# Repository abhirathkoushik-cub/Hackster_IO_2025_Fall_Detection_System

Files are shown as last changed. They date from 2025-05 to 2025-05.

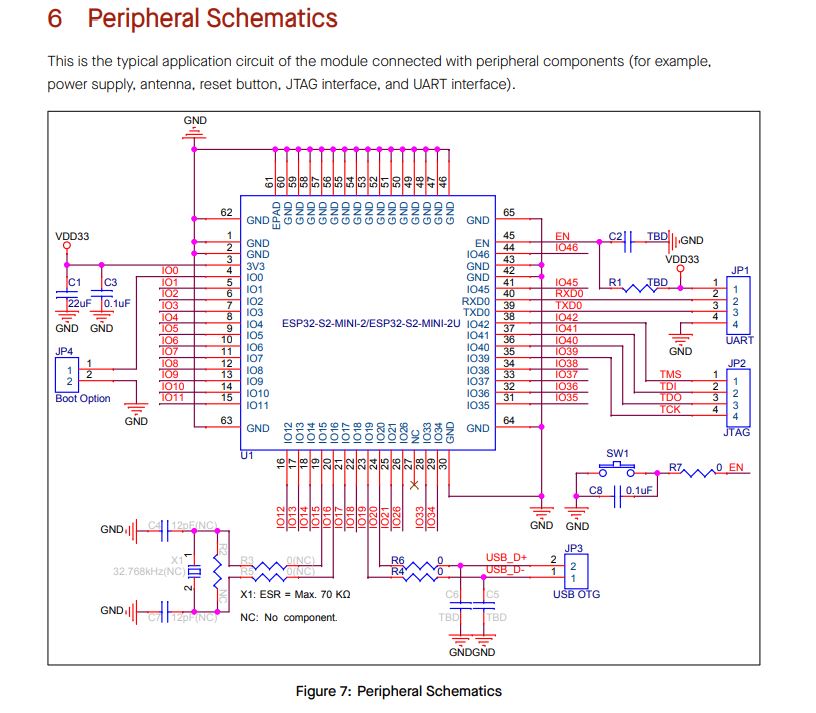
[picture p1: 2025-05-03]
Design Documentation/DATA_SHEETS/Capture1.JPG

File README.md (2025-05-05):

This Repository contains the Code, PCB and Schematic Files for the Sentinel-Fall: Smart Radar Based Fall Detection System project done for Hackster IO Competition 2025.

Project Link: https://www.hackster.io/sentinel-fall/sentinel-fall-smart-radar-based-fall-detection-system-265fd4#toc---step-2---firmware-programming---esp32--amp--nrf54l15-11 

Project Contributers: Abhirath Koushik, Nikhil Bhat and Vrushabh Gada

My Individual Contribution is for the NRF BLE Alert Configuring and Programming, 
https://github.com/abhirathkoushik-cub/Hackster_IO_2025_Fall_Detection_System/tree/main/Program%20Files/Demo%20Code%20Files/NRF%20BLE%20Alerts%20(Dev%20Kit)

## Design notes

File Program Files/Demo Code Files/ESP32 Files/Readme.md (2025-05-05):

# Author

Vrushabh Gada

# Software Tools:
    Arduino ide (Used to write and program the esp32)
# Hardware:
    ESP32

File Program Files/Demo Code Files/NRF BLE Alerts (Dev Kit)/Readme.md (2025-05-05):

## Author 
Abhirath Koushik (abhirathkoushik-cub)

# Software Tools:
1. nRF Connect VS Code Externsion (For Programming the nRF54L15 DK/SoC)
2. nRF Connect for Desktop (For viewing and interacting with the Serial Terminal)
3. nRF Connevt for Mobile (For viewing the BLE Alerts on the phone. Can also be used to send back a message and enable bi-directional communication)

# Hardware:
1. nRF54L15 DK
2. Arduino Uno (Used for testing my program by providing alternative high-low pulses on the GPIO Pin of the DK)

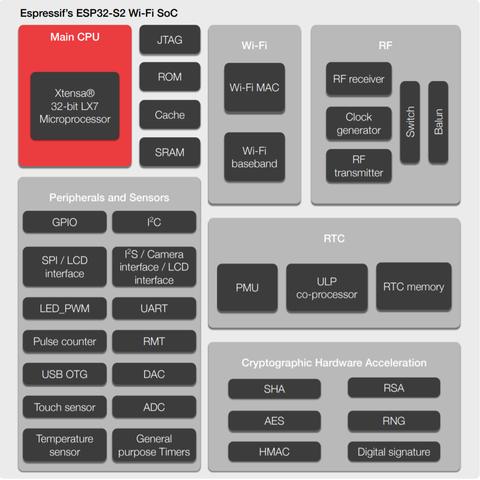
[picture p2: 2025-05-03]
Design Documentation/DATA_SHEETS/NRF_SOC/NRF_PROJ336/NRF_PROJ/param.jpg

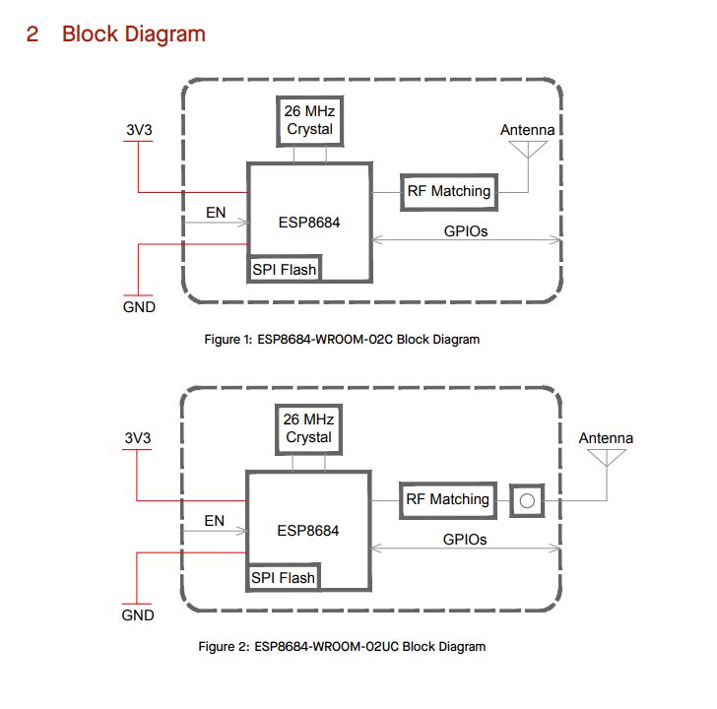
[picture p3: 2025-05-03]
Design Documentation/DATA_SHEETS/NRF_SOC/NRF_PROJ336/NRF_PROJ/Capture.JPG

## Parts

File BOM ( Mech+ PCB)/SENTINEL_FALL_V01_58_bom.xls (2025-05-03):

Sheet: SENTINEL_FALL_pcb_bom
Item | Quantity | Reference | Value | MFG Part Number | MFG Name | BOM NOTE | PCB Footprint
1 | 2 | C1,C37 | 10uF | CNC5L1X7R1H106K160AE | TDK | NA | C1206 | note: refer next sheet for mechanical bom
2 | 2 | C2,C17 | 1uF | C1206R105K3RACT250 | KEMET | NA | C1206
3 | 4 | C3,C6,C10,C73 | 4.7uF | CC1206KKX7R9BB475 | YAGEO | NA | C1206
4 | 14 | C4,C11,C12,C15,C18,C20,C21,C23,C24,C38,C39,C71,C72,C75 | 10uF | GCM31CD71H106KE36K | Murata Electronics | NA | C1206
5 | 1 | C5 | 47nF | C1206C473F5GECAUTO | KEMET | NA | C1206
6 | 3 | C7,C8,C9 | 22uF | C2012X5R1V226M125AC | TDK | NA | C0805
7 | 2 | C13,C14 | 47uF | GRM31CR61C476ME44K | Murata Electronics | NA | C1206
8 | 8 | C16,C25,C26,C27,C28,C30,C74,C76 | 100nF | C1206C104K5RACTU | KEMET | NA | C1206
9 | 2 | C29,C31 | 2.2uF | CL31B225KOHNNNE | Samsung Electro-Mechanics | NA | C1206
10 | 1 | C32 | 10nF | MSASU105SB7103KFNA01 | Taiyo Yuden | NA | C1206
11 | 3 | C33,C35,C36 | 18pF | VJ1206A180JXXPW1BC | Vishay Vitramon | NA | C1206
12 | 1 | D2 | DIODE | B260A-13-F | Diodes Inc | NA | DIOM5226X230N
13 | 1 | FB1 | 120R, 0.2A | BLM21RK121SN1D | Murata Electronics | NA | F0805
14 | 6 | FD1,FD2,FD3,FD4,FD5,FD6 | TEST POINT_SMD | NOT APPLICABLE | NOT APPLICABLE | NA | 40-t_global_fid
15 | 2 | J1,J8 | USB4105-GF-A | USB4105-GF-A | GCT | NA | GCT_USB4105-GF-A
16 | 2 | J5,J6 | 2X5 HDR JLINK | 3220-10-0300-00 | CNC Tech | NA | CNC_3220-10-0300-00
17 | 1 | J7 | HEADER 2/SM_5 | S2B-PH-SM4-TB | JST Sales America Inc. | NA | JST_S2B-PH-SM4-TB
18 | 1 | J11 | PH1-06-UA | PH1-06-UA | Adam Tech | NA | HDRV6W64P0X254_1X6_1524X250X952P
19 | 1 | L1 | 1uH | IHLP2525CZER1R0M01 | Vishay Dale | NA | IND_IHLP2525CZER1R0M01
20 | 1 | L2 | 4.7uH | MLZ1608M4R7WT000 | TDK Corporation | NA | L0603
21 | 7 | R2,R3,R14,R15,R32,R33,R34 | 10K | RC1206FR-0710KL | TE Connectivity | NA | R1206
22 | 12 | R4,R5,R12,R16,R19,R24,R27,R28,R29,R30,R35,R46 | 4K7 | RC1206FR-074K7L | YAEGO | NA | R1206
23 | 4 | R6,R7,R8,R9 | 4K7 | RC1206FR-074K7L | YAEGO | NA | R1206
24 | 2 | R10,R13 | 0R | RC1206JR-070RL | YAGEO | NA | R1206
25 | 2 | R11,R31 | 1M | TNPW12061M00BEEA | Vishay Dale | NA | R1206
26 | 1 | R17 | 1.05K, 0p1% | TNPW12061K05BEEN | Vishay / Dale | NA | R1206
27 | 1 | R18 | 6.8K,0p1% | ERA-8AEB682V | Panasonic Electronic Components | NA | R1206
28 | 6 | R23,R37,R39,R40,R41,R45 | 1K | RCWP12061K00FKS2 | Vishay / Dale | NA | R1206
29 | 2 | R26,R47 | 100R | RC1206FR-7W100RL | YAGEO | NA | R1206
30 | 1 | R36 | 500m | RCWE1206R500FKEA | Vishay Dale | NA | R1206
31 | 3 | R42,R43,R44 | 5k6 | ERJ-S08F5601V | Panasonic | NA | R1206
32 | 1 | SW1 | 500SSP3S1M6QEA | 500SSP3S1M6QEA | E-Switch | NA | 500SSP3S1M6QEA
33 | 3 | SW6,SW7,SW8 | SW_TC_SPST_1 | KMR221NGLFS | C&K | NA | KMR221_CNK
34 | 1 | SW9 | BD04AV | BD04AV | C&K | NA | BD04AV
35 | 10 | TP2,TP3,TP4,TP12,TP13,TP14,TP15,TP16,TP20,TP21 | TEST POINT_2 | NA | NA | NA | TP40
36 | 4 | TP6,TP17,TP18,TP19 | T POINT R | NA | NA | NA | mh7p5_3p2t
37 | 1 | U1 | TVS DIODE | TVS2200DRVR | TI | NA | SON65P200X200X80-7N
38 | 1 | U2 | BQ25886RGE | BQ25886RGER | Texas Instruments | NA | QFN50P400X400X100-25N
39 | 2 | U3,U4 | MYLSM00502ERPL | MYLSM00502ERPL | Murata | NA | MURATA_MYLSM00502ERPL
40 | 1 | U5 | MCP1727-3302ESN | MCP1727-3302E/SN | Microchip Technology | NA | SOIC127P600X175-8N
41 | 1 | U6 | ESP32-S3-MINI | ESP32-S3-MINI-1-N8 | Espressif Systems | NA | ESP32-S3-MINI-1U_EXP
42 | 1 | U7 | SIM8000L | SIM8000L MODULE | ElectroPeak 3.4/5 | NA | SIM8000L
43 | 4 | U8,U9,U10,U11 | IN-PI55QATPRPGPBPW-40 | IN-PI55QATPRPGPBPW-30 | Inolux | NA | INPI55QATPRPGPBPW30
44 | 1 | U12 | BC818-40LT1G | BC818-40LT1G | onsemi | NA | SOT95P237X111-3N
45 | 1 | U13 | AT-1224-TWT-5V-2-R | AT-1224-TWT-5V-2-R | PUI Audio, Inc. | NA | XDCR_AT-1224-TWT-5V-2-R
46 | 1 | U14 | NRF54L15-QFAA-R | NRF54L15-QFAA-R | Nordic Semiconductors | NA | QFN40P600X600X90-49N
47 | 1 | U15 | SEN0623 | SEN0623 | DF ROBOT | NA | SEN0623
48 | 1 | U16 | EKMB1101111 | EKMB1101111 | Panasonic Electric Works | NA | EKMB1101111
49 | 1 | U17 | SSM3J332R | SSM3J332R,LF | Toshiba Electronic Devices Storage Corp. | NA | SOT95P240X88-3N
50 | 1 | X1 | 32 MHz | MP06003 | Golledge Electronics Ltd | NA | XTAL_ABM11W-330000MHZ-8-D1X-T3
NOTE: | note: refer next sheet for mechanical bom

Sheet: MECH BOM
 | FASTNERS, SCREWS, NUTS
SL NO | DESCRIPTION | QTY
1 | 6-6 Male-Female Threaded Hex Standoff (M3X12) | 4
2 | Aluminum Hex Nut(M3) | 4
3 | Stainless Steel Hex Drive Flat Head Screw(M3X6) | 10
4 | 95610A104_Nylon Plastic Washer (M3) | 6
5 | Steel Socket Head Screw (M2.5X6) | 2
6 | Aluminum Hex Nut(M2.5) | 2
 | 3D PRINT FILES
SL NO | DESCRIPTION | QTY
1 | BOTTOM CONTAINER | 1
2 | TOP LID | 1
3 | BRACKET-1 | 1
4 | BRACKET-2 | 1
 | OTHER ITEMS
SL NO | DESCRIPTION | QTY | Link
1 | 7.4V 2600mAh Rechargeable Li-ion Battery with JST 2Pin, 2.0 | 1 | https://www.amazon.com/dp/B0DSZNX3YP?ref=ppx_yo2ov_dt_b_fed_asin_title
2 | Car Phone Holder Mobile Phone Holder Stand | 1 | https://www.aliexpress.us/item/3256802910592284.html
3 | Segger J link Cable | 1 | https://www.digikey.com/en/products/detail/adafruit-industries-llc/1675/6827142

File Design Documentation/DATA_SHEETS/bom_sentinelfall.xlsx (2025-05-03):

 | Component | Description | Quantity | Source
1 | nRF54L15 | Nordic Semiconductor BLE SoC | 1 | Nordic Semiconductor | finalized | https://www.mouser.com/ProductDetail/Nordic-Semiconductor/NRF54L15-CAAA-R?qs=QpmGXVUTftEz0ltGbbtKyA%3D%3D
2 | 101990981 | 24GHz mmWave Radar Module (Doppler Radar, Sleep Detection) | 1 | Seeed Studio | finalized | 101990981
3 | ESP32-S2FH4 | RF TXRX MOD WIFI PCB TRACE SMD | 1 | espressif | finalized | https://www.digikey.com/en/products/detail/espressif-systems/ESP32-S2FH4/14553010
4 | SIM800L | Smallest SIM800L GPRS GSM Breakout Module Quad-Band 850/900/1800/1900MHz SIM Card Slot Onboard with Antenna 3.7~4.2V | 1 | amazon |  | https://electropeak.com/sim800l-gprs-gsm-sms-microsim-module?gQT=2
5 | AM312 | HiLetgo 3pcs AM312 Mini Pyroelectric PIR Human Sensor Module PIR Infrared IR Sen | 1 |  |  | https://www.amazon.com/HiLetgo-Pyroelectric-Sensor-Infrared-Detector/dp/B07RT7MK7C
6 | BQ25306 | A 1-2 Cell Buck Battery Charger | 1
 | BQ25723 | Buck-Boost Battery Charger | 1 | Various Suppliers
 | ESP32-WROOM (Replacing EBYTE E34-2G4H in the design) | WiFi + BLE Module | 1 | Espressif
 | SIM800L | GSM Module with MIC & Headphone Jack | 1 | M5Stack
 | AM312 | Mini Pyroelectric PIR Sensor | 1 | Various Suppliers
 | Turnigy 5000mAh 4S 25C LiPo Pack w/XT-90 | High-capacity battery | 1 | Turnigy / HobbyKing

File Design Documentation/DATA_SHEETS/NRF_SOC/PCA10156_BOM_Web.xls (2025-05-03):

Bill of material
Board: | PCA10156
Version: | 0.8.1
Designator | Value | Description | Fitted | Footprint Doc | Manufacturer | Manufacturer Part Number
C1, C2 | 2.2µF | Capacitor, Ceramic, 2.2µF 2.5V X6T 0201,±20% | Fitted | 0201 | Murata | GRM033R61A225KE47
C3, C10 | 10µF | Capacitor, X6S, ±20%, 6.3V | Fitted | 0402 | N.A. | N.A.
C4, C7, C8, C11, C13, C14, C15, C16, C18, C20, C21, C22, C29, C34, C35, C36, C37, C44, C46, C48, C49, C52, C53, C55 | 100nF | Capacitor, X5R, ±10% | Fitted | 0201 | N.A. | N.A.
C5 | 18pF | Capacitor, C0G, ±5%, 25V | Fitted | 0201 | Walsin Technology Corporation | 0201N180J250CT
C6 | 0.9pF | Capacitor, C0G, ±0.1pF, 25V | Fitted | 0201 | Murata | GJM0335C1ER90BB01D
C9 | 0.6pF | Capacitor, C0G, ±0.1pF, 25V | Fitted | 0201 | Murata | GJM0335C1ER60BB01
C12, C30 | 10nF | Capacitor, X7R, ±10% | Fitted | 0201 | N.A. | N.A.
C17, C19 | 300pF | Capacitor, C0G, ±5%, 50V | Fitted | 0402 | N.A. | N.A.
C23 | 2.2µF | Capacitor, X5R, ±10% | Fitted | 0402 | N.A. | N.A.
C24, C25, C26, C27, C28 | 10µF | Capacitor, X7T, ±20%, 10V | Fitted | 0603 | Murata | GRM188D71A106MA73
C31, C32, C38, C39, C45 | 1.0µF | Capacitor, X5R, ±10%, 6.3V | Fitted | 0402 | N.A. | N.A.
C33 | 2.2nF | Capacitor, X7R, ±10%, 10V | Fitted | 0201 | N.A. | N.A.
C40 | 1.4pF | Capacitor, C0G, ±0.05pF, 25V | Fitted | 0201 | Murata | GJM0335C1E1R4WB01D
C41 | 100nF | Capacitor, X7R, ±10% | Not Fitted | 0402 | N.A. | N.A.
C42, C43, C54 | 4.7µF | Capacitor, X7S, ±10%, 10V | Fitted | 0603 | N.A. | N.A.
C47 | 1.0µF | Capacitor, Ceramic, X5R, ±10%, 16V | Fitted | 0402 | Murata | GRT155R61C105KE01D
C50 | 10nF | Capacitor, X7R, ±10% | Not Fitted | 0201 | N.A. | N.A.
C51 | TBD | Chip Cap 0201 | Not Fitted | 0201 | N.A. | N.A.
C56 | 100nF | Capacitor, X5R, ±10% | Not Fitted | 0201 | N.A. | N.A.
D1 | PRTR5V0U2X | Ultra low capacitance double rail-to-rail ESD protection diode | Fitted | SOT-143B | NXP Semiconductors | PRTR5V0U2X
FB1 | 120R/0.2A | Ferrite Bead, 120 Ohm @ 100MHz, 200mA, 500 mOhm Max | Fitted | 0201 | Murata | BLM03AG121SN1D
FB2 | 120R/0.55A | Ferrite Bead, 120 Ohm @ 100MHz, 500mA, 250 mOhm Max | Fitted | 0402 | Murata | BLM15AG121SN1D
Fid1, Fid2, Fid3 | N.A. | Fiducial Mark | Fitted | Fiducial | N.A. | N.A.
J1 | MM8130-2600 | Coaxial Connector with Switch | Fitted | COAXIAL-SWF | Murata | MM8130-2600
J3 | USB-C 2.0 | USB-C Receptacle, 16 Pin, USB 2.0 | Fitted | SD-80259-001 | Bellweather Electronic Corp. | SD-80259-1021
J7 | FPC 0.5mm RA SMD | 0.5mm FPC, 5P,Right Angle SMT,Double Contact,H=1.2mm,White, Tin plated | Fitted | FPC_05P-0.5mm-RA-SMD | WCON | 5141-05RZDNWR03
JP1 | Shunt 2.54mm | Shunt Jumper 2.54mm Black, open top | Fitted | SHUNT JUMPER 2.54mm | Samtec | SNT-100-BK-T
L1 | 4.7µH | Inductor, 120mA, ±20%, 0.65R | Fitted | 0603 | TDK Corporation | MLZ1608M4R7WT000
L2 | 1.6nH | Inductor, 1000mA, ±0.05ｎH, 50mOhm | Fitted | 0201 | Murata | LQP03HQ1N6W02
L3 | 3.5nH | Inductor, 500mA, ±0.1ｎH, 170mOhm | Fitted | 0201 | Murata | LQP03HQ3N5B02
L4 | 1.2nH | Inductor, 1100mA, ±0.05ｎH, 40mOhm | Fitted | 0201 | Murata | LQP03HQ1N2W02
L8, L9 | 2.2µH | Inductor, Irms=2.5A, Isat=2.9A, ±20%, DCR=73mΩ | Fitted | 0806 | Samsung Electro-Mechanics America | CIGT201610EH2R2MNE
LABEL1 | 12x12mm | PCA version label, stick-on, 12x12mm | Fitted | Label | Ellco Etikett | A33512‐01
LD1, LD2, LD3, LD4, LD5 | L0603G | LED, Green, 0603, 573nm, Vf=2.0V, 24mcd, - 40 to +85°C | Fitted | 0603 | Victory Electronics | VS 25C7M5
P0, P1, P2 | Pin Hdr 2x10 | Pin Header 2x10, 2.54mm (100mil) SMD | Fitted | HDR_2x10-SMD-2.54MM | WCON | 1125-1210S0M116CR09
P4 | Pin List 1x3 | Pin List 1x3, 2.54mm (100mil) | Not Fitted | LIST_1x3 | N.A. | N.A.
P6 | Pin List 1x3 | Pin List 1x3, 2.54mm (100mil), SMD | Fitted | LIST_1x3_SMD | WCON | 1125-1103S0M116CR04
P15, P19 | Pin Header 2x5, 1.27mm | Pin Header 2x5, 1.27mm (50mil), SMD, Keying Shroud | Fitted | HDR_2x5-SMD-1.27mm | WCON | 3132-10MS0BK00R5
P16 | Pin Header 2x10, 1.27mm | Pin Header 2x10, 1.27mm (50mil), SMD, Keying Shroud | Not Fitted | HDR_2x10-SMD-1.27mm | WCON | 3132-20MS0BK00R1
P30, P31, P32 | Pin Header 2x2 SMD | Pin Header 2x2, SMD, 2.54mm (100mil) | Fitted | HDR_2x2-SMD | WCON | 1125-1202S0M116CR03
Q1, Q2, Q3 | NX138AKS | MOSFET 2N-CH 60V 0.17A TSSOP6 (SOT363) | Fitted | TSSOP6 | Nexperia | NX138AKSX
Q6 | PBSS4330PA | 30V, 3A, 2.1W, G=270, NPN Transistor | Fitted | HUSON-3 (2x2) | Nexperia | PBSS4330PA,115
R1, R2, R19, R20 | 220R | Resistor, ±1%, 0.05W | Fitted | 0201 | N.A. | N.A.
R3 | 4k7 | Resistor, ±1%, 0.05W | Fitted | 0201 | N.A. | N.A.
R5 | 560R | Resistor, ±1%, 0.05W | Fitted | 0201 | N.A. | N.A.
R6, R8, R13, R14, R15, R16, R17, R23, R55, R56 | 100k | Resistor, ±1%, 0.05W | Fitted | 0201 | N.A. | N.A.
R7 | 47R | Resistor, ±1%, 0.05W | Fitted | 0201 | N.A. | N.A.
R10, R11, R12, R18, R27 | 1M0 | Resistor, ±1%, 0.05W | Fitted | 0201 | N.A. | N.A.
R21, R22 | 0R | Resistor, ±5%, 0.063W | Fitted | 0402 | N.A. | N.A.
R24 | TBD | Chip Res 0402 | Not Fitted | 0402 | N.A. | N.A.
R25 | 270k | Resistor, ±1%, 0.05W | Fitted | 0201 | N.A. | N.A.
R26 | 47k | Resistor, ±1%, 0.05W | Fitted | 0201 | N.A. | N.A.
R28 | 33k | Resistor, ±1%, 0.05W | Fitted | 0201 | N.A. | N.A.
R29, R30 | 18k | Resistor, ±1%, 0.05W | Not Fitted | 0201 | N.A. | N.A.
R31, R32, R35 | 0R | Resistor, ±5%, 0.05W | Fitted | 0201 | N.A. | N.A.
R33, R34 | 0R | Resistor, ±5%, 0.063W | Not Fitted | 0402 | N.A. | N.A.
R36 | 1k | Resistor, ±1%, 0.05W | Fitted | 0201 | N.A. | N.A.
R54 | 0R | Resistor, ±5%, 0.05W | Not Fitted | 0201 | N.A. | N.A.
SW1, SW2, SW3, SW5, SW6 | PB SW | Tactile Switch, SPNO, SMD, 160gf, 6.2x6.3x2.5mm | Fitted | Switch-PB-6.2x6.3mm-SMD | Dailywell | TS604VM1-025BR-R
SW4 | MK-22D14-G2 | Slide Switch DPDT | Fitted | MK-22D14-G2 | HUA-JIE CORP. | MK-22D14-G2
TP22 | TP | PC TEST POINT TIN SMD L | Fitted | Harwin S1751-46R | Harwin | S1751-46R
U1 | nRF54L15-QFAABB0 | Multi-protocol Bluetooth Low Energy, IEEE 802.15.4, ANT and 2.4GHz proprietary system-on-chip | Fitted | QFN-48 | Nordic Semiconductor | nRF54L15-QFAABB0
U2 | nRF5340-QKAA | Multi-protocol Bluetooth Low Energy, IEEE 802.15.4, ANT and 2.4GHz proprietary system-on-chip | Fitted | AQFN-98 | Nordic Semiconductor | nRF5340-QKAAD0
U3 | TLV271 | Dual rail to rail CMOS Amplifier | Fitted | SOT-25 | Diodes Incorporated | TLV271CW5-7
U4, U5, U6 | FSA2466UMX | Data / Audio Low-Voltage Dual DPDT Analog Switch | Fitted | UFQFN-16 | ON Semiconductor | FSA2466UMX
U7, U8 | TXB0302 | 2-bit bidirectional voltage-level translator with automatic direction sensing | Fitted | XFDFN-8 | Texas Instruments | TXB0302DQMR
U9 | MX25R6435F | Ultra low power, 64M-bit, serial multi I/O flash memory | Fitted | WSON-8 | Macronix | MX25R6435FZNIL0
U10 | nPM1300-QEAAC0 | Li-Ion/Li-Polymer USB-C battery charger with high efficiency buck regulators, LDOs or load switches, LED drivers, TWI and VBUSOUT | Fitted | QFN-32 | Nordic Semiconductor | nPM1300-QEAAC0
X1 | 32.768kHz | XTAL SMD 2012, 32.768kHz, 9pF, ±20ppm | Fitted | XTAL_2012 | TXC Corporation | 9HT11-32.768KDZC-T
X2, X3 | 32MHz | XTAL SMD 2016, 32MHz, Cl=8pF, Tol: ±10ppm, Stab: ±15ppm | Fitted | XTAL_2016 | Golledge | MP06003
 |  | Pin Header 2x5, 1.27mm

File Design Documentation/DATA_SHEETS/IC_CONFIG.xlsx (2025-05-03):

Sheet: Sheet1
 | Component | Description | Quantity | Source
1 | nRF54L15 | Nordic Semiconductor BLE SoC | 1 | Nordic Semiconductor | finalized | https://www.mouser.com/ProductDetail/Nordic-Semiconductor/NRF54L15-CAAA-R?qs=QpmGXVUTftEz0ltGbbtKyA%3D%3D
2 | 101990981 | 24GHz mmWave Radar Module (Doppler Radar, Sleep Detection) | 1 | Seeed Studio | finalized | 101990981
3 | ESP32-S2-SOLO-2-N4 | RF TXRX MOD WIFI PCB TRACE SMD | 1 | espressif | finalized | https://www.digikey.com/en/products/detail/espressif-systems/ESP32-S2FH4/14553010
4 | SIM800L | Smallest SIM800L GPRS GSM Breakout Module Quad-Band 850/900/1800/1900MHz SIM Card Slot Onboard with Antenna 3.7~4.2V | 1 | amazon | finalized | https://electropeak.com/sim800l-gprs-gsm-sms-microsim-module?gQT=2
5 | AM312 | HiLetgo 3pcs AM312 Mini Pyroelectric PIR Human Sensor Module PIR Infrared IR Sen | 1 | amazon | finalized | https://www.amazon.com/HiLetgo-Pyroelectric-Sensor-Infrared-Detector/dp/B07RT7MK7C
6 | BQ25886 | A 1-2 Cell Buck Battery Charger | 1 | amazon | finalized
 |  | PWR RAILS
 |  | 5 | 3.3 | 4 | PWR
1 | nRF54L15 |  | 80 |  | 264
2 | 101990981 | 100 |  |  | 500
3 | ESP32-S2-SOLO-2-N4 |  | 500 |  | 1650
4 | SIM800L |  |  | 2000 | 8000 | PEAK
5 | AM312 |  | 1 |  | 3.3
 |  |  |  |  | 10.4173 | PEAK
 |  | 100 | 581
 |  | 0.1A | 3.3A | 2A
 |  | PWR TREE
 |  | tell me 1 ldo THAT can convert from 2s batetry to 5v, 5v to 3v3 , 5v to 4v .
 |  |  | LTM4705 | FOR 3V3
 |  |  | TPS7B82-Q1 | FOR 5V0
 | BQ25723 | Buck-Boost Battery Charger | 1 | Various Suppliers
 | ESP32-WROOM (Replacing EBYTE E34-2G4H in the design) | WiFi + BLE Module | 1 | Espressif
 | SIM800L | GSM Module with MIC & Headphone Jack | 1 | M5Stack
 | AM312 | Mini Pyroelectric PIR Sensor | 1 | Various Suppliers
 | Turnigy 5000mAh 4S 25C LiPo Pack w/XT-90 | High-capacity battery | 1 | Turnigy / HobbyKing

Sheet: Sheet4
https://www.mouser.com/ProductDetail/Texas-Instruments/TPSM84338RCJR?qs=7%2F6SraaimPTVMRXxZgYtyw%3D%3D
MYLSM00502ERPL

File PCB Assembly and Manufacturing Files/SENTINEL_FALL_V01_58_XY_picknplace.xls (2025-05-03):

Design Name E:/nn/GERBER/BOARD/SENTINEL_FALL_V01.brd
Date Tue Apr 08 22:40:18 2025
Total Placed Components: &nbsp136
Placed Component Report
REFDES | COMP_DEVICE_TYPE | COMP_VALUE | COMP_TOL | SYM_NAME | SYM_X | SYM_Y | SYM_ROTATE | SYM_MIRROR
C1 | CAP_CER_10UF_50V_1206_X7R_10P_C | 10uF |  | C1206 | 1649 | 2868 | 270 | NO
C2 | CAP_1UF_25V_1206_10P0_C1206_1UF | 1uF |  | C1206 | 1413.472 | 2123 | 90 | YES
C3 | CAP_CER_4700NF_50V_X7R_1206_C12 | 4.7uF |  | C1206 | 2105 | 2755 | 0 | NO
C4 | CAP_10UF_50V X7T_1206_C1206_10U | 10uF |  | C1206 | 1508 | 2123 | 270 | YES
C5 | 8_CAP_47NF_1206_C1206_47NF | 47nF |  | C1206 | 1930 | 2280 | 270 | YES
C6 | CAP_CER_4700NF_50V_X7R_1206_C12 | 4.7uF |  | C1206 | 2155 | 2580 | 90 | NO
C7 | 4_CAP_ 22UF 20% X5R_0805 35VDC_ | 22uF |  | C0805 | 1711 | 2421 | 180 | YES
C8 | 4_CAP_ 22UF 20% X5R_0805 35VDC_ | 22uF |  | C0805 | 1711 | 2338 | 180 | YES
C9 | 4_CAP_ 22UF 20% X5R_0805 35VDC_ | 22uF |  | C0805 | 1711 | 2505.213 | 180 | YES
C10 | CAP_CER_4700NF_50V_X7R_1206_C12 | 4.7uF |  | C1206 | 1578 | 2654 | 270 | YES
C11 | CAP_10UF_50V X7T_1206_C1206_10U | 10uF |  | C1206 | 1430 | 2485 | 0 | NO
C12 | CAP_10UF_50V X7T_1206_C1206_10U | 10uF |  | C1206 | 916.118 | 2459 | 180 | NO
C13 | CAP_CER_47UF_16V_X5R_1206_C1206 | 47uF |  | C1206 | 1258 | 2085.016 | 270 | NO
C14 | CAP_CER_47UF_16V_X5R_1206_C1206 | 47uF |  | C1206 | 566 | 2137 | 180 | NO
C15 | CAP_10UF_50V X7T_1206_C1206_10U | 10uF |  | C1206 | 2055 | 2365 | 90 | NO
C16 | CAP_100NF_50V_1206_X7R_C1206_10 | 100nF |  | C1206 | 2042 | 2075 | 270 | YES
C17 | CAP_1UF_25V_1206_10P0_C1206_1UF | 1uF |  | C1206 | 1825 | 2095 | 90 | NO
C18 | CAP_10UF_50V X7T_1206_C1206_10U | 10uF |  | C1206 | 1800 | 1070 | 270 | NO
C20 | CAP_10UF_50V X7T_1206_C1206_10U | 10uF |  | C1206 | 1896 | 1070 | 270 | NO
C21 | CAP_10UF_50V X7T_1206_C1206_10U | 10uF |  | C1206 | 174 | 2728 | 0 | NO
C23 | CAP_10UF_50V X7T_1206_C1206_10U | 10uF |  | C1206 | 350 | 1052.738 | 90 | NO
C24 | CAP_10UF_50V X7T_1206_C1206_10U | 10uF |  | C1206 | 540 | 575 | 180 | NO
C25 | CAP_100NF_50V_1206_X7R_C1206_10 | 100nF |  | C1206 | 930 | 1015 | 0 | NO
C26 | CAP_100NF_50V_1206_X7R_C1206_10 | 100nF |  | C1206 | 255.013 | 1052.738 | 90 | NO
C27 | CAP_100NF_50V_1206_X7R_C1206_10 | 100nF |  | C1206 | 930 | 920 | 0 | NO
C28 | CAP_100NF_50V_1206_X7R_C1206_10 | 100nF |  | C1206 | 316 | 783 | 180 | NO
C29 | CAP_CER_2.2UF_16V_X7R_1206_C120 | 2.2uF |  | C1206 | 406 | 1372 | 0 | YES
C30 | CAP_100NF_50V_1206_X7R_C1206_10 | 100nF |  | C1206 | 628 | 423 | 90 | NO
C31 | CAP_CER_2.2UF_16V_X7R_1206_C120 | 2.2uF |  | C1206 | 900 | 770 | 0 | NO
C32 | 7_CAP_10NF_10P_50V_C1206_10NF | 10nF |  | C1206 | 783 | 1471 | 180 | YES
C33 | CAP_18PF_125V_1206_C1206_18PF | 18pF |  | C1206 | 783 | 1372 | 180 | YES
C35 | CAP_18PF_125V_1206_C1206_18PF | 18pF |  | C1206 | 1010.137 | 606.252 | 180 | NO
C36 | CAP_18PF_125V_1206_C1206_18PF | 18pF |  | C1206 | 1230.609 | 606.252 | 0 | NO
C37 | CAP_CER_10UF_50V_1206_X7R_10P_C | 10uF |  | C1206 | 1076.567 | 2868 | 270 | NO
C38 | CAP_10UF_50V X7T_1206_C1206_10U | 10uF |  | C1206 | 1801 | 1790 | 90 | NO
C39 | CAP_10UF_50V X7T_1206_C1206_10U | 10uF |  | C1206 | 1925 | 2095 | 270 | NO
C71 | CAP_10UF_50V X7T_1206_C1206_10U | 10uF |  | C1206 | 1597 | 609 | 0 | NO
C72 | CAP_10UF_50V X7T_1206_C1206_10U | 10uF |  | C1206 | 1155 | 1785 | 270 | NO
C73 | CAP_CER_4700NF_50V_X7R_1206_C12 | 4.7uF |  | C1206 | 2182 | 580 | 90 | NO
C74 | CAP_100NF_50V_1206_X7R_C1206_10 | 100nF |  | C1206 | 2150 | 2365 | 90 | NO
C75 | CAP_10UF_50V X7T_1206_C1206_10U | 10uF |  | C1206 | 285 | 605 | 270 | NO
C76 | CAP_100NF_50V_1206_X7R_C1206_10 | 100nF |  | C1206 | 1850 | 1615 | 0 | NO
D2 | B260A-13-F_DIOM5226X230N_DIODE | DIODE |  | DIOM5226X230N | 460 | 1621 | 270 | YES
FB1 | FB_120R_200MA_0805_F0805_120R, | 120R, 0.2A |  | F0805 | 597 | 1372 | 180 | YES
FD1 | TEST POINT_SMD_0_40-T_GLOBAL_FI | TEST POINT_SMD |  | 40-T_GLOBAL_FID | 385 | 100 | 0 | NO
FD2 | TEST POINT_SMD_0_40-T_GLOBAL_FI | TEST POINT_SMD |  | 40-T_GLOBAL_FID | 385 | 100 | 0 | YES
FD3 | TEST POINT_SMD_0_40-T_GLOBAL_FI | TEST POINT_SMD |  | 40-T_GLOBAL_FID | 1985 | 100 | 0 | YES
FD4 | TEST POINT_SMD_0_40-T_GLOBAL_FI | TEST POINT_SMD |  | 40-T_GLOBAL_FID | 1985 | 100 | 0 | NO
FD5 | TEST POINT_SMD_0_40-T_GLOBAL_FI | TEST POINT_SMD |  | 40-T_GLOBAL_FID | 385 | 3215 | 0 | NO
FD6 | TEST POINT_SMD_0_40-T_GLOBAL_FI | TEST POINT_SMD |  | 40-T_GLOBAL_FID | 385 | 3215 | 0 | YES
J1 | CONN_USB_USB4105-GF-A_GCT_USB41 | USB4105-GF-A |  | GCT_USB4105-GF-A | 1726 | 3251 | 180 | NO
J5 | HEADER_10_2X5_SHROUDED_CNC_3220 | 2X5 HDR JLINK |  | CNC_3220-10-0300-00 | 2133 | 1160 | 90 | NO
J6 | HEADER_10_2X5_SHROUDED_CNC_3220 | 2X5 HDR JLINK |  | CNC_3220-10-0300-00 | 1585 | 245 | 0 | NO
J7 | HEADER 2/SM_5_JST_S2B-PH-SM4-TB | HEADER 2/SM_5 |  | JST_S2B-PH-SM4-TB | 314.189 | 2473 | 90 | NO
J8 | CONN_USB_USB4105-GF-A_GCT_USB41 | USB4105-GF-A |  | GCT_USB4105-GF-A | 1088.567 | 3251 | 180 | NO
J11 | HEADER_6_6X1_MALE_HDRV6W64P0X25 | PH1-06-UA |  | HDRV6W64P0X254_1X6_1524X250X952P | 519.96 | 220.75 | 0 | NO
L1 | IND_1UH_11A_1_UKPKG_IND_IHLP252 | 1uH |  | IND_IHLP2525CZER1R0M01 | 1711 | 2101 | 270 | YES
L2 | IND_4.7UH_350MA_500MOHM_SM_L060 | 4.7uH |  | L0603 | 472 | 1115 | 0 | NO
R2 | RES_10K_1W4_1P0_1206_R1206_10K | 10K |  | R1206 | 1657.102 | 2868 | 90 | YES
R3 | RES_10K_1W4_1P0_1206_R1206_10K | 10K |  | R1206 | 1775.213 | 2868 | 90 | YES
R4 | RES_4K7_1W4_1P0_1206_R1206_4K7 | 4K7 |  | R1206 | 1178 | 2316 | 180 | YES
R5 | RES_4K7_1W4_1P0_1206_R1206_4K7 | 4K7 |  | R1206 | 1387 | 2654 | 90 | YES
R6 | RES_4K7_1W4_1P0_1206_R1206_4K7 | 4K7 |  | R1206 | 1128 | 2123 | 270 | YES
R7 | RES_4K7_1W4_1P0_1206_R1206_4K7 | 4K7 |  | R1206 | 1223 | 2123 | 270 | YES
R8 | RES_4K7_1W4_1P0_1206_R1206_4K7 | 4K7 |  | R1206 | 1033 | 2123 | 90 | YES
R9 | RES_4K7_1W4_1P0_1206_R1206_4K7 | 4K7 |  | R1206 | 1318 | 2123 | 90 | YES
R10 | RES_0R0_1W4_1P0_1206_R1206_0R | 0R |  | R1206 | 1292 | 2654 | 270 | YES
R11 | RES_1M_1W2_0P1_1206_R1206_1M | 1M |  | R1206 | 1178 | 2507 | 0 | YES
R12 | RES_4K7_1W4_1P0_1206_R1206_4K7 | 4K7 |  | R1206 | 1482 | 2654 | 270 | YES
R13 | RES_0R0_1W4_1P0_1206_R1206_0R | 0R |  | R1206 | 1178 | 2412 | 0 | YES
R14 | RES_10K_1W4_1P0_1206_R1206_10K | 10K |  | R1206 | 1578 | 2654 | 90 | NO
R15 | RES_10K_1W4_1P0_1206_R1206_10K | 10K |  | R1206 | 1674 | 2654 | 270 | NO
R16 | RES_4K7_1W4_1P0_1206_R1206_4K7 | 4K7 |  | R1206 | 1248 | 2336.984 | 90 | NO
R17 | RES_1P05K_0W52_0P1_1206_R1206_1 | 1.05K, 0p1% |  | R1206 | 1729 | 2195.252 | 90 | NO
R18 | RES_6P8K_1W4_0P1_1206_R1206_6.8 | 6.8K,0p1% |  | R1206 | 1094 | 2192.252 | 90 | NO
R19 | RES_4K7_1W4_1P0_1206_R1206_4K7 | 4K7 |  | R1206 | 618 | 2333.984 | 90 | NO
R23 | RES_1K_1W4_1P0_1206_R1206_1K | 1K |  | R1206 | 1238 | 456 | 90 | YES
R24 | RES_4K7_1W4_1P0_1206_R1206_4K7 | 4K7 |  | R1206 | 1745 | 1940 | 0 | NO
R26 | RES_100R_1W8_1P0_1206_R1206_100 | 100R |  | R1206 | 797 | 1687 | 270 | YES
R27 | RES_4K7_1W4_1P0_1206_R1206_4K7 | 4K7 |  | R1206 | 723 | 423 | 270 | NO
R28 | RES_4K7_1W4_1P0_1206_R1206_4K7 | 4K7 |  | R1206 | 586.627 | 1181.748 | 90 | NO
R29 | RES_4K7_1W4_1P0_1206_R1206_4K7 | 4K7 |  | R1206 | 681.627 | 1181.748 | 90 | NO
R30 | RES_4K7_1W4_1P0_1206_R1206_4K7 | 4K7 |  | R1206 | 2182 | 774 | 270 | NO
R31 | RES_1M_1W2_0P1_1206_R1206_1M | 1M |  | R1206 | 1120.373 | 498.252 | 0 | NO
R32 | RES_10K_1W4_1P0_1206_R1206_10K | 10K |  | R1206 | 524 | 2334 | 270 | NO
R33 | RES_10K_1W4_1P0_1206_R1206_10K | 10K |  | R1206 | 1019.669 | 2868 | 90 | YES
R34 | RES_10K_1W4_1P0_1206_R1206_10K | 10K |  | R1206 | 1137.78 | 2868 | 90 | YES
R35 | RES_4K7_1W4_1P0_1206_R1206_4K7 | 4K7 |  | R1206 | 316 | 879.407 | 180 | NO
R36 | RES_500MOHM_1W2_1P0_1206_R1206_ | 500m |  | R1206 | 2050 | 2580 | 90 | NO
R37 | RES_1K_1W4_1P0_1206_R1206_1K | 1K |  | R1206 | 660.788 | 2971 | 180 | NO
R39 | RES_1K_1W4_1P0_1206_R1206_1K | 1K |  | R1206 | 655 | 2735 | 180 | NO
R40 | RES_1K_1W4_1P0_1206_R1206_1K | 1K |  | R1206 | 457.638 | 3055 | 0 | NO
R41 | RES_1K_1W4_1P0_1206_R1206_1K | 1K |  | R1206 | 406.235 | 2151.495 | 90 | NO
R42 | RES_GENRIC_5K6_1W4_1P0_1206_R12 | 5k6 |  | R1206 | 449.764 | 2735 | 0 | NO
R43 | RES_GENRIC_5K6_1W4_1P0_1206_R12 | 5k6 |  | R1206 | 347.402 | 2950 | 0 | NO
R44 | RES_GENRIC_5K6_1W4_1P0_1206_R12 | 5k6 |  | R1206 | 305.377 | 2096.08 | 0 | NO
R45 | RES_1K_1W4_1P0_1206_R1206_1K | 1K |  | R1206 | 1625 | 1776.882 | 90 | NO
R46 | RES_4K7_1W4_1P0_1206_R1206_4K7 | 4K7 |  | R1206 | 2210 | 1810 | 270 | NO
R47 | RES_100R_1W8_1P0_1206_R1206_100 | 100R |  | R1206 | 1135 | 566.236 | 90 | YES
SW1 | SWITH_PWR_RA_0_500SSP3S1M6QEA_5 | 500SSP3S1M6QEA |  | 500SSP3S1M6QEA | 1905 | 2510 | 90 | YES
SW6 | SW_TC_SPST_1_KMR221_CNK_SW_TC_S | SW_TC_SPST_1 |  | KMR221_CNK | 1989 | 1814.002 | 0 | NO
SW7 | SW_TC_SPST_1_KMR221_CNK_SW_TC_S | SW_TC_SPST_1 |  | KMR221_CNK | 718 | 3178.002 | 0 | NO
SW8 | SW_TC_SPST_1_KMR221_CNK_SW_TC_S | SW_TC_SPST_1 |  | KMR221_CNK | 455 | 398.998 | 180 | NO
SW9 | SW_RA_DIP_BD04AV_BD04AV | BD04AV |  | BD04AV | 2042.422 | 800.988 | 90 | YES
TP2 | TEST POINT_2_TP40_TEST POINT_2 | TEST POINT_2 |  | TP40 | 1825 | 2990 | 0 | NO
TP3 | TEST POINT_2_TP40_TEST POINT_2 | TEST POINT_2 |  | TP40 | 2050 | 2840 | 180 | NO
TP4 | TEST POINT_2_TP40_TEST POINT_2 | TEST POINT_2 |  | TP40 | 504.813 | 3183.242 | 0 | NO
TP6 | T POINT R_MH7P5_3P2T_T POINT R | T POINT R |  | MH7P5_3P2T | 160 | 3192.75 | 0 | NO
TP12 | TEST POINT_2_TP40_TEST POINT_2 | TEST POINT_2 |  | TP40 | 646 | 2551 | 0 | NO
TP13 | TEST POINT_2_TP40_TEST POINT_2 | TEST POINT_2 |  | TP40 | 1169.567 | 2927 | 0 | NO
TP14 | TEST POINT_2_TP40_TEST POINT_2 | TEST POINT_2 |  | TP40 | 1197.013 | 183.738 | 180 | YES
TP15 | TEST POINT_2_TP40_TEST POINT_2 | TEST POINT_2 |  | TP40 | 1931.813 | 187.222 | 0 | NO
TP16 | TEST POINT_2_TP40_TEST POINT_2 | TEST POINT_2 |  | TP40 | 1410.813 | 3081.882 | 0 | NO
TP17 | T POINT R_MH7P5_3P2T_T POINT R | T POINT R |  | MH7P5_3P2T | 160 | 160 | 0 | NO
TP18 | T POINT R_MH7P5_3P2T_T POINT R | T POINT R |  | MH7P5_3P2T | 2202.133 | 3192.75 | 0 | NO
TP19 | T POINT R_MH7P5_3P2T_T POINT R | T POINT R |  | MH7P5_3P2T | 2202.133 | 160 | 0 | NO
TP20 | TEST POINT_2_TP40_TEST POINT_2 | TEST POINT_2 |  | TP40 | 2250 | 2555 | 0 | NO
TP21 | TEST POINT_2_TP40_TEST POINT_2 | TEST POINT_2 |  | TP40 | 1885 | 1925 | 0 | NO
U1 | IC_TVS_DIODE_SON65P200X200X80-7 | TVS DIODE |  | SON65P200X200X80-7N | 1762 | 2867 | 90 | NO
U2 | BQ25886RGER_QFN50P400X400X100-2 | BQ25886RGE |  | QFN50P400X400X100-25N | 1472 | 2391 | 180 | YES
U3 | MYLSM00502ERPL_MURATA_MYLSM0050 | MYLSM00502ERPL |  | MURATA_MYLSM00502ERPL | 1481 | 2211 | 180 | NO
U4 | MYLSM00502ERPL_MURATA_MYLSM0050 | MYLSM00502ERPL |  | MURATA_MYLSM00502ERPL | 861 | 2208 | 180 | NO
U5 | MCP1727-3302ESN_SOIC127P600X175 | MCP1727-3302ESN |  | SOIC127P600X175-8N | 2100 | 2110 | 90 | NO
U6 | ESP32-S3-MINI_ESP32-S3-MINI-1U_ | ESP32-S3-MINI |  | ESP32-S3-MINI-1U_EXP | 1393 | 1172 | 180 | NO
U7 | SIP_IC_SIM800L_0_SIM8000L_SIM80 | SIM8000L |  | SIM8000L | 708.032 | 1983.74 | 270 | YES
U8 | IN-PI55QATPRPGPBPW-40_INPI55QAT | IN-PI55QATPRPGPBPW-40 |  | INPI55QATPRPGPBPW30 | 1446.284 | 448.126 | 0 | YES
U9 | IN-PI55QATPRPGPBPW-40_INPI55QAT | IN-PI55QATPRPGPBPW-40 |  | INPI55QATPRPGPBPW30 | 1731 | 447 | 90 | YES
U10 | IN-PI55QATPRPGPBPW-40_INPI55QAT | IN-PI55QATPRPGPBPW-40 |  | INPI55QATPRPGPBPW30 | 1731 | 741 | 180 | YES
U11 | IN-PI55QATPRPGPBPW-40_INPI55QAT | IN-PI55QATPRPGPBPW-40 |  | INPI55QATPRPGPBPW30 | 1446.284 | 741 | 270 | YES
U12 | NPN_TRANSISTOR_BC818-40LT1G_SOT | BC818-40LT1G |  | SOT95P237X111-3N | 631.221 | 1704.055 | 0 | YES
U13 | BUZZER_AT-1224-TWT-5V-2-R_XDCR_ | AT-1224-TWT-5V-2-R |  | XDCR_AT-1224-TWT-5V-2-R | 332 | 1621 | 180 | NO
U14 | NRF54L15-QFAA-R_QFN40P600X600X9 | NRF54L15-QFAA-R |  | QFN40P600X600X90-49N | 586.627 | 838.126 | 0 | NO
U15 | SIP_SEN0623_SEN0623_SEN0623 | SEN0623 |  | SEN0623 | 144 | 553 | 180 | YES
U16 | PIR_SIP_EKMB1101111_EKMB1101111 | EKMB1101111 |  | EKMB1101111 | 1288 | 1732 | 0 | YES
U17 | SSM3J332R,LF_SOT95P240X88-3N_SS | SSM3J332R |  | SOT95P240X88-3N | 517 | 2515 | 90 | NO
X1 | XTAL_32MHZ_XTAL_ABM11W-330000MH | 32 MHz |  | XTAL_ABM11W-330000MHZ-8-D1X-T3 | 1126.373 | 378.252 | 90 | NO

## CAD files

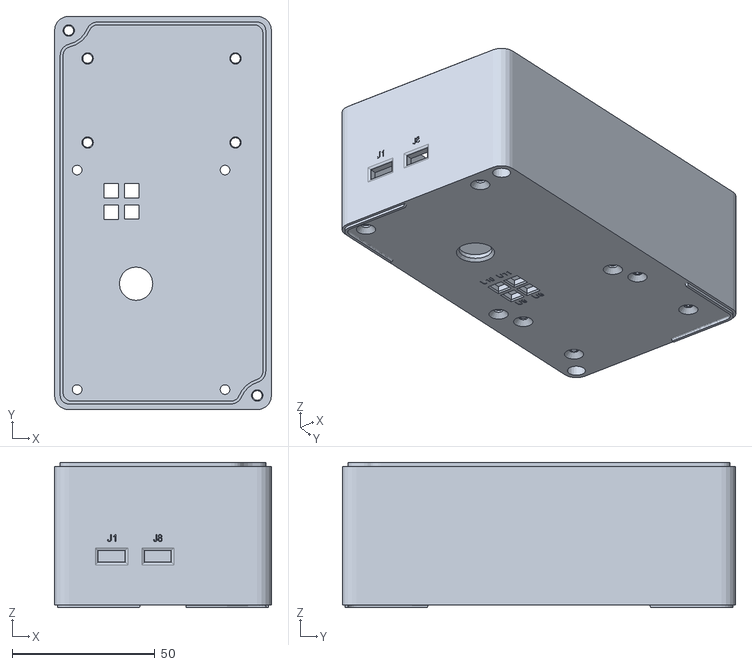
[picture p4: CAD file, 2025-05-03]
3D Files ( Top, Bottom Lid, Mounting Brackets)/MOUNTING CONTAINER BOTTOM PART_stp.stl
76.1 x 138.0 x 51.0

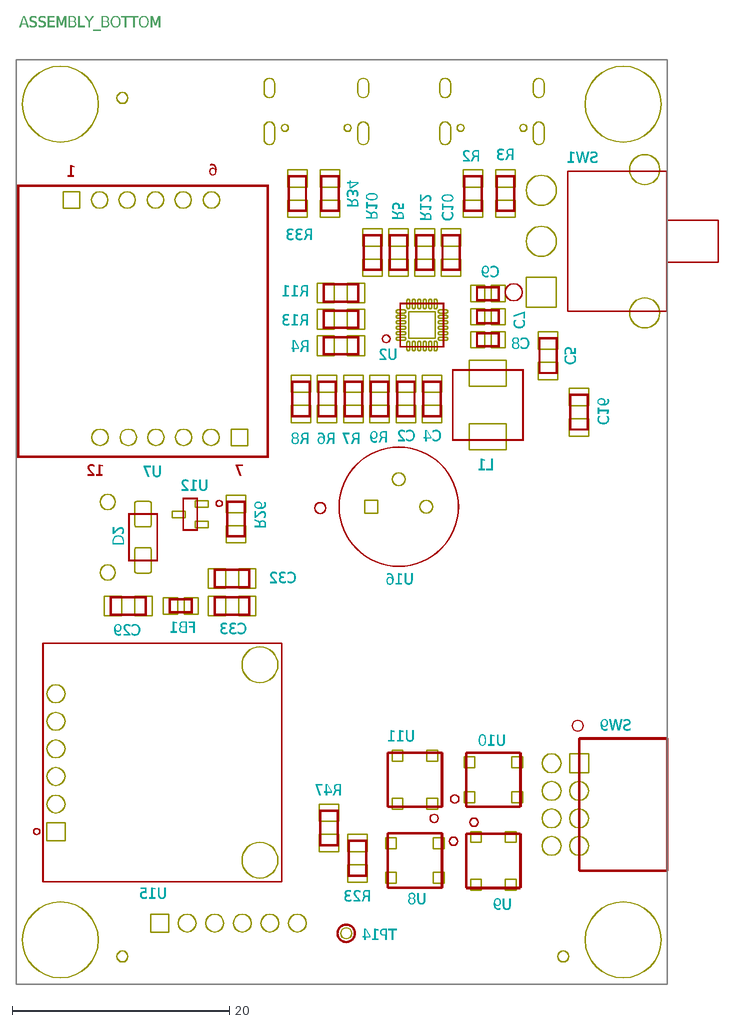
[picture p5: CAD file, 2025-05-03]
PCB Assembly and Manufacturing Files/MECHANICAL/DXF/BOTTOM.dxf
U12
D2
U11
U8
U10
U9
L1
C33
C29
C10
C16
C2
C4
C5
C32
R8
R10
R4
R3
R12
R13
R2
R23
R7
R6
R11
R9
R26
R33
R5
R34
R47
TP14
C9
C8
C7
U2
FB1
6
1
7
12
U7
U15
SW9
U16
SW1
ASSEMBLY_BOTTOM

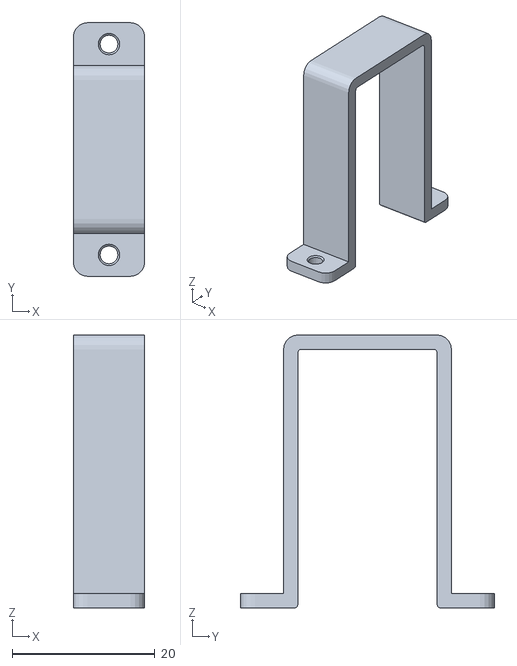
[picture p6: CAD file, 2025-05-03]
3D Files ( Top, Bottom Lid, Mounting Brackets)/BRACKET.stl
10.0 x 35.5 x 38.2

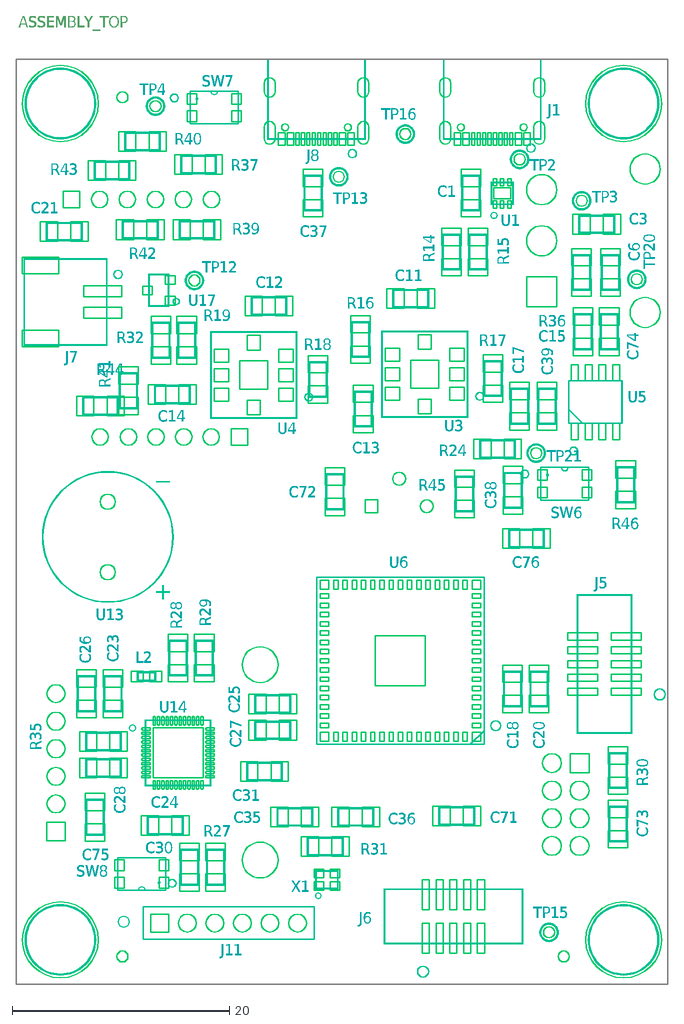
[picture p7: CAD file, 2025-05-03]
PCB Assembly and Manufacturing Files/MECHANICAL/DXF/TOP.dxf
X1
U17
J7
U5
U1
U6
C76
C35
C36
C31
C6
C3
C37
C12
C1
C17
C11
C15
C18
C20
C21
C23
C24
C38
C25
C14
C26
C27
C28
C30
C13
C72
C39
C71
C73
C75
C74
R42
R43
R44
R18
R19
R24
R14
R15
R16
R17
R31
R32
R29
R30
R27
R28
R36
R41
R40
R39
R37
R35
R45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

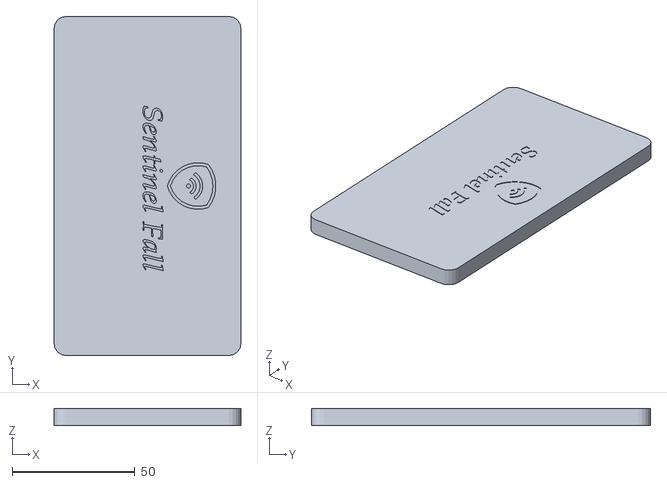
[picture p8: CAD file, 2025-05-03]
3D Files ( Top, Bottom Lid, Mounting Brackets)/MOUNTING CONTAINER LID.stl
76.1 x 138.0 x 7.00

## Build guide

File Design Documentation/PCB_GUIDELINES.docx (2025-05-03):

PCB GUIDELINES:

USE THIS STACKUP:

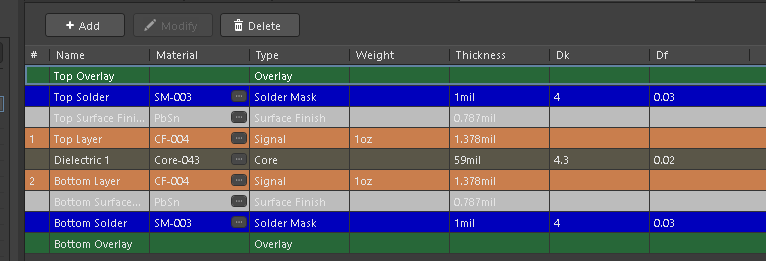
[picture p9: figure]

KEEP LINE WIDTH >6 MILS FOR ALL TRaCES.

| VOLATGE (V) | CURRENT (A) | ALL LAYERS | TO KEEP V DROPS < 0.15V, 10 DEG ABOVE AMBIENT
VSYS | 7.4 | 2.66063473 | 50 MILS | <3 INCHES
V3V3 | 3.3 | 0.8 | 25 MILS | <6 INCHES
V4V0 | 4 | 2.2 | 35 MILS | <3 INCHES
V5V0 | 5 | 1 | 25 MILS | <6 INCHES

• Download Saturn PCB Toolkit and don’t exceed 0.1 V voltage drop. If u don’t understand this step pls refer the table above. Keep the ambient temperature at 25 °C and max temperature rise at 10 °C.

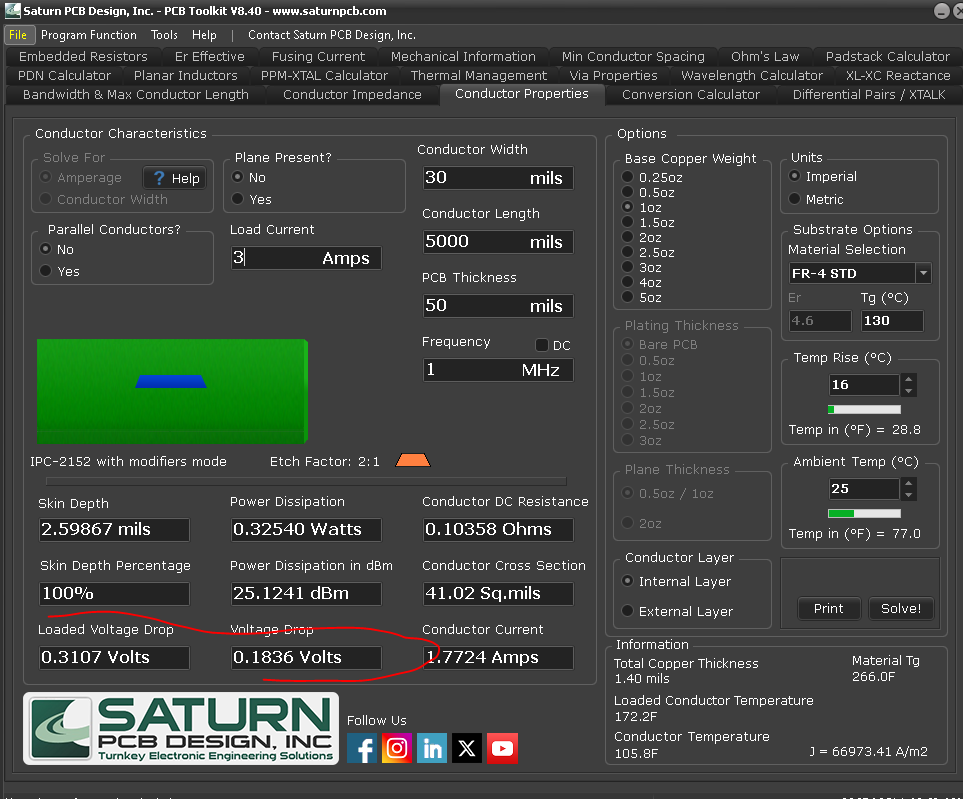
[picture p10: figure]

• Keep W = 2H for 50 Ω USB (DP, DN) traces. Use 3W spacing for loose coupling.

• Keep other signals at >2W spacing from I2C lines.

• Place the crystal close to the MCU with >20 mil clearance from other traces.

• Place decoupling capacitors (decaps) as close as possible to the power pins.

• Maintain a continuous return path for all USB. Use reference vias FOR EVERY 4 GPIOS.

• Use 10–25 mil vias (each can carry ~1.4 A for your stackup).

Use multiple vias (at least 2–3) for power transitions for all PWR NETS.

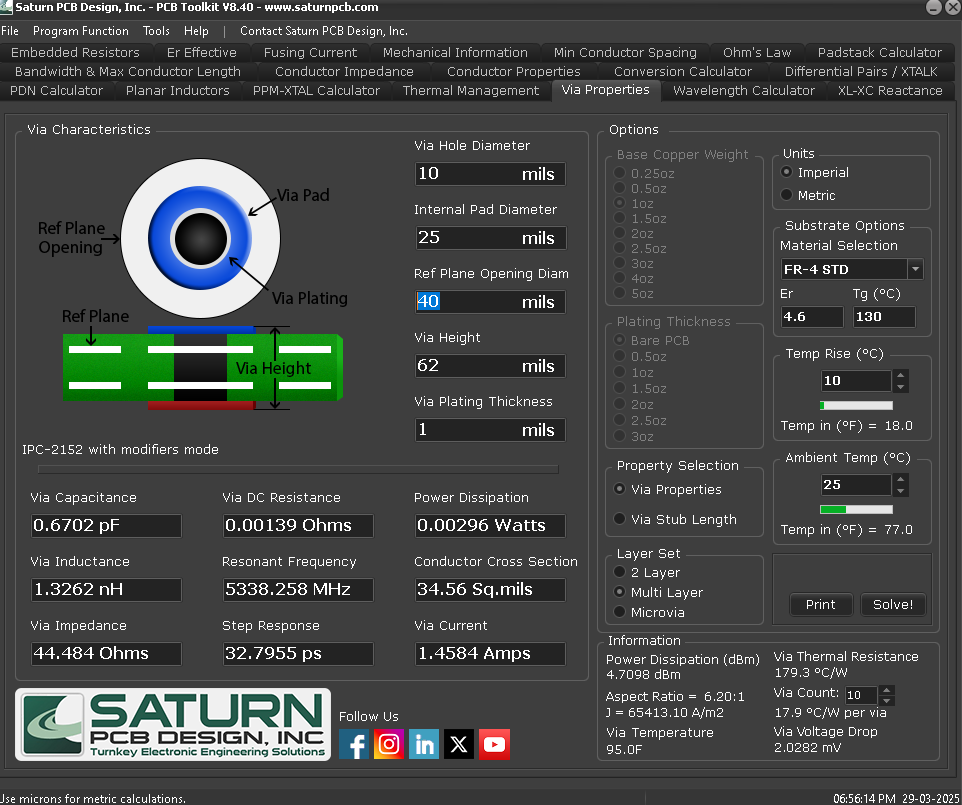
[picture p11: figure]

•Add silkscreen for all connectors. Label pin numbers or signal names — shorthand is okay.

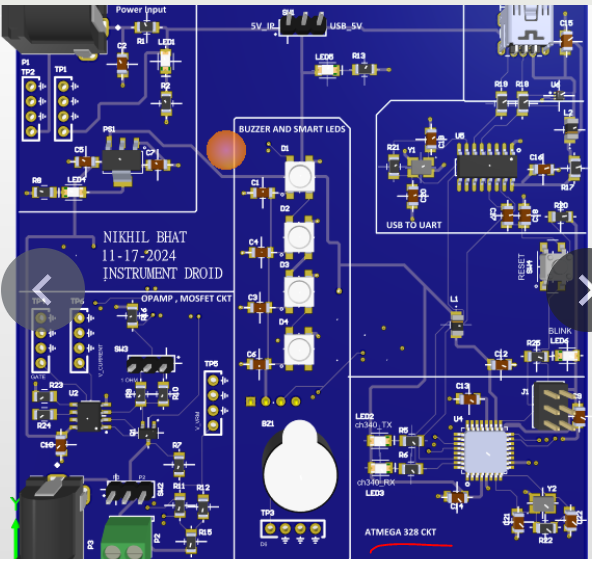
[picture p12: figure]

• PLEASE put silk markings this way otherwise there tehre will be problems with pcb assembly and eventually the brd.

https://www.pcbway.com/smt_ordering_guide.html

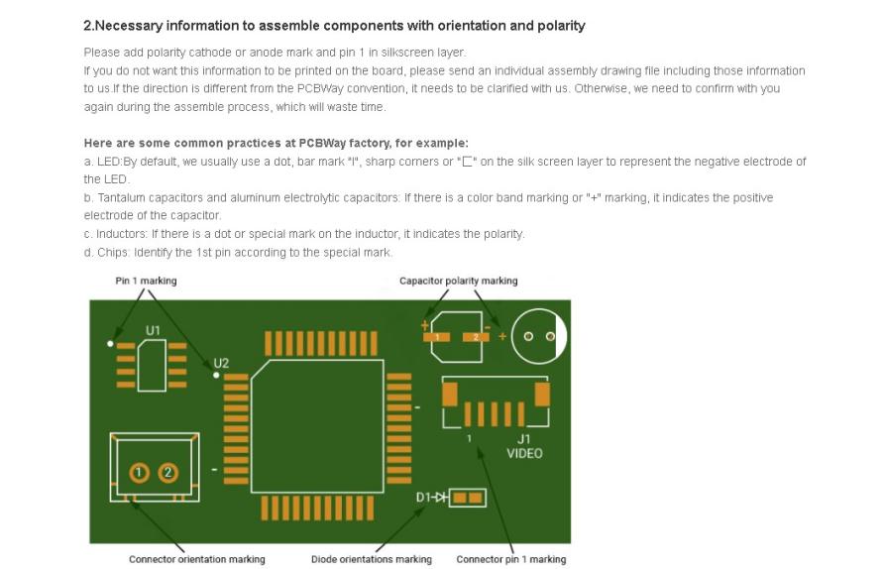
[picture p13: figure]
WhatsApp Image 2025-04-05 at 20.59.21_6e780d14

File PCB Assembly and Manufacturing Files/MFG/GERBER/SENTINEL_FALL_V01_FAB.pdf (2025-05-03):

### ART FILM - FAB

### ART FILM - FAB

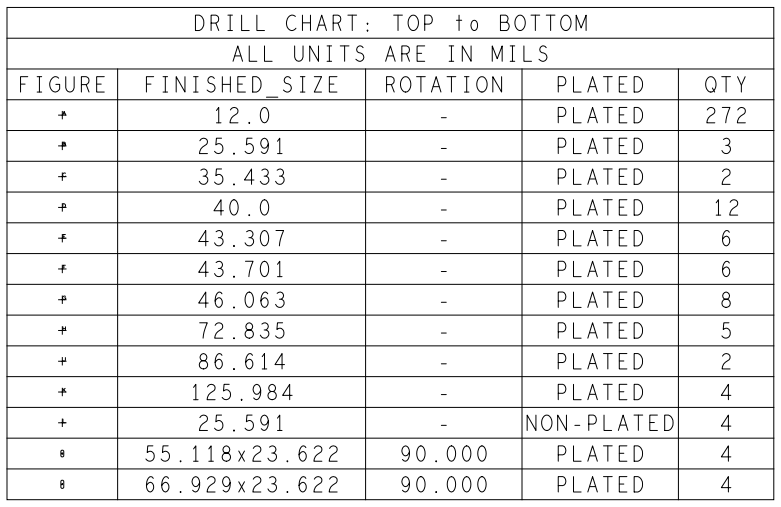
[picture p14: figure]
FIGURE; FINISHED_SIZE; DRILL CHART:; TOP; to BOTTOM; ALL UNITS ARE IN MILS; ROTATION; NON-PLATED; PLATED; QTY

### 2.FOUR LAYER, 1.6MM PCB THICKNESS, NO IMPEDANCE CONTROL

### 1.BOARD DIMENSIONS ARE IN MM

### NOTES:

FAB_DRAWING

60

85.16

13.0 Surface finish ENIG

12.1 Add the | Auto | serial number in the | area provided near "SL/NO"
12.0 Test | coupons need | to be provided.
11.0 Automatic optical inspection of | all layers is required.

11.Inspection:

10.0 Bow and twist | to | be .007 | IN/IN or .090 max according to IPC-A-600K.

10.Bow and Twist:

9.0 There shall be | max | of 25 units per package wrapped | in sulpher | and | silicon

9.Packaging:

8.1 Finished boards | must conform to 0.01 MG/IN max NAcl | ionic contamonation
8.0 Boards shall be free | of fiber glass dust or any other forgien material.

8.Cleanlines:

7.1 Apply | test stamp in non | legend area on the | solder side of PCB.
7.0 All boards shall | be 100% elecrically tested for | open/shorts.

7.Electrical Test:

6.3 Registration to be +/- .005 and must pass peel test.

6.2 Minimum clearance | between silkscreen | legend and vias, pads or holes , to be
6.1 No Silkscreen | allowed on exposed lands or in holes (burnout with soldermask)
6.0 Silksceen using white non-conductive epoxy or equivalent | ( both sides ).

6.Silkscreen:

5.2 If applicable, Gold | plat edge fingers | over low | stress nickel:
5.1 Finished boardsshall not have | nicks, scratches, voids, exposed copper,
5.0 Plate | thru with copper .0010 min | to .002 max thickness drill size.

5.Finish:

4.3 An CNC drill file has | been supplied - see drill table.
4.2 All holes | diameters | to be +/- .003 unless | otherwise specified.
4.1 All holes | to | be +/- | .003 | from the true postion unless | otherwise specified.
4.0 All hole diameters | are finished sizes.
4. Drilling:
3.0 Soldermask both sides | with | (green | color) liquid photoimageble soldermask

3.Soldermask:

2.1 Color is vendor's option.

2.0 NEMA | Grade FR-4/Epoxy | class , | foil lamination structure for core and

2.Material:

1.1 This | drawing | is to be used in | conjuction with | the provided gerber and
1.0 Producibility study- it is the responsibility of | the supplier to conduct

1.Specifications:

NOTES:

surrounding material to | prevent | shipping | damage.
free material and contained | in heavy | cardboard cartons with sufficient

.005.

Minimum gold thickness | : | .00003
Maximum nickel thickness: | .0005
poor plating, | or misdrilled holes.
dimensions apply after | plating.
.003 max. thickness. Soldermask over bare | copper.
copper thickness: type GFN, Grade | A, Class 1, Class A.
drill | data | when applicable.

cannot met.

conformance to the customers standards, and of any specifications that changes, revisions, or corrections made or recommendations to ensure

customer must be advised | in writing (inadvance of manufacturing) of | any

thorough review of the artwork and media for manufacturablity in the

supplier's process | compliance to all | applicable specifications. | The

MM is two numeric month and XXX is three numeric running serial number.

in the | format of "YYMMXXX"where YY is two numeric year
as measured bu omega | meter 600SMD.

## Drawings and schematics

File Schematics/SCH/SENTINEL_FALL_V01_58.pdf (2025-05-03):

# SENTINEL FALL V1 SCH

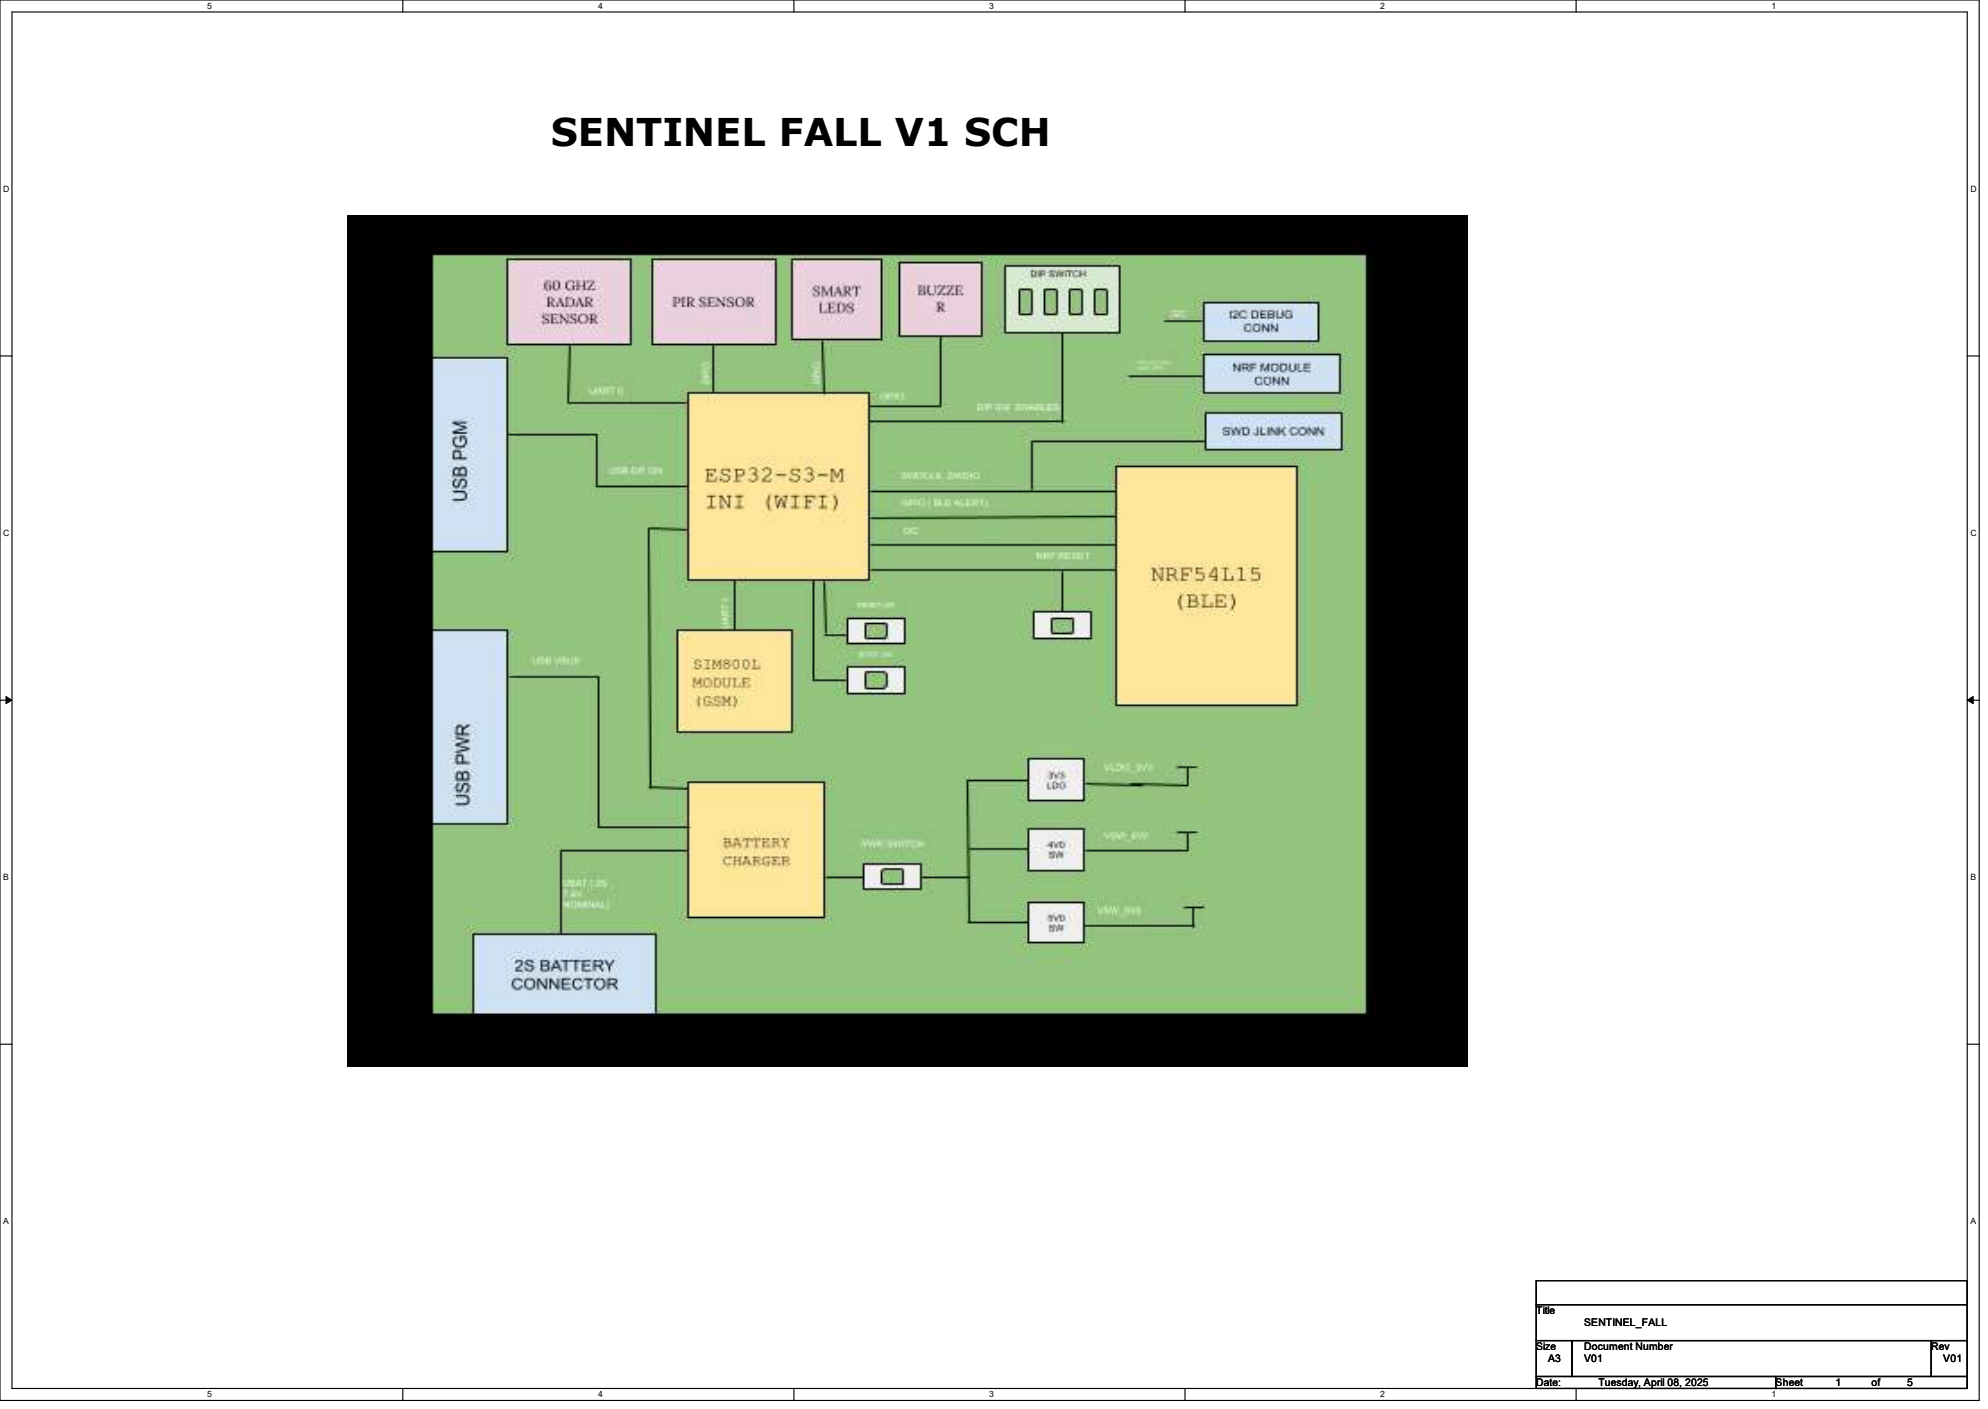
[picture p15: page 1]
Title Size; Document Number; Rev Date:; Sheet; V01 SENTINEL_FALL A3; Tuesday, April 08, 2025; 5 Title Size

# USB C - PORT1 - POWER

# USB C - PORT2 - PGM

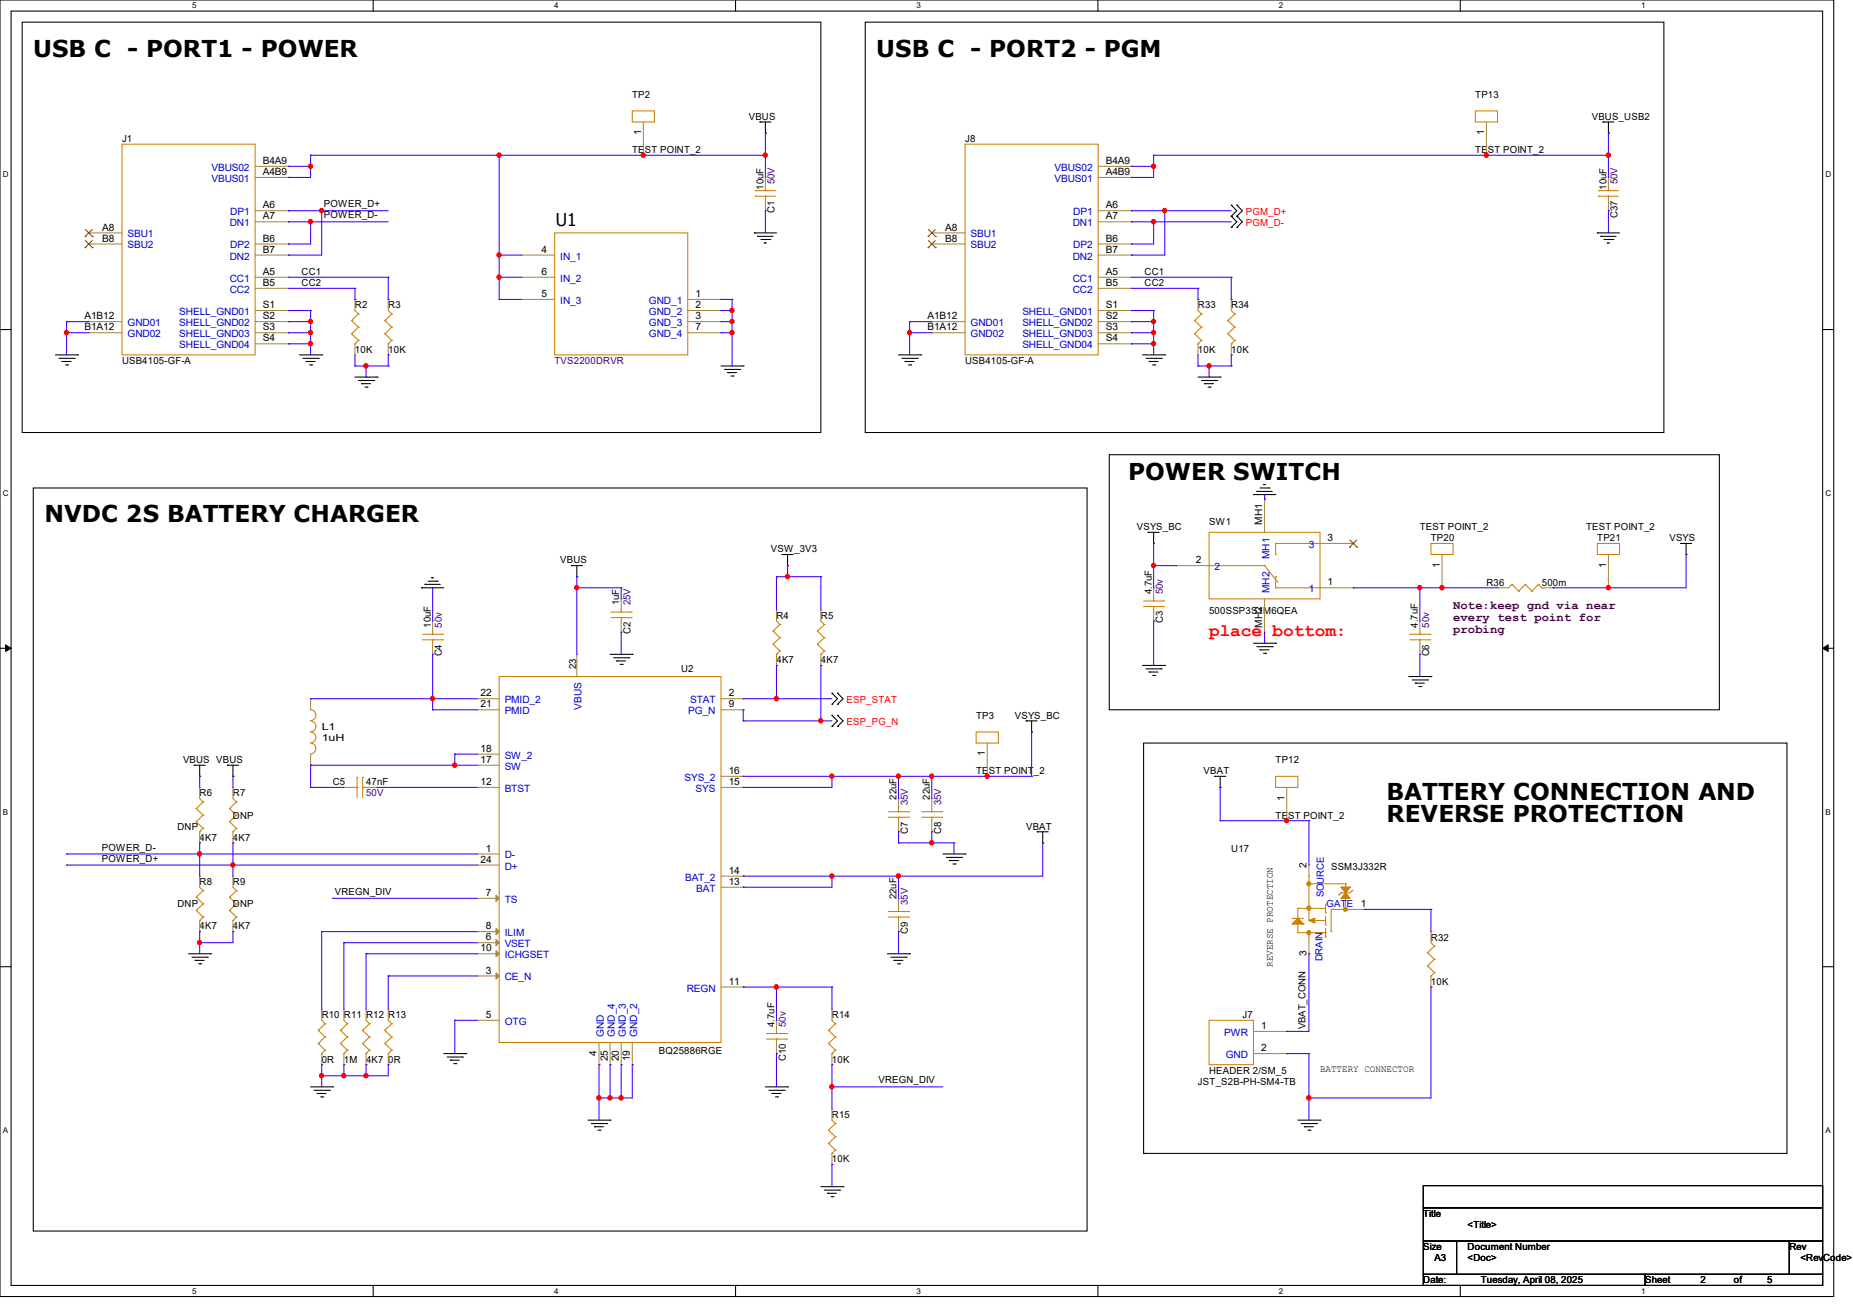
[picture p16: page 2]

2 MH² MH² MH¹ MH¹

Note:keep gnd via near
every test point for
probing

TP12 TEST POINT_2
BATTERY CONNECTION AND REVERSE PROTECTION

5V0 SW OP | 4V0 SW OP
VSYS | VSW_5V0 | VSYS | VSW_4V0

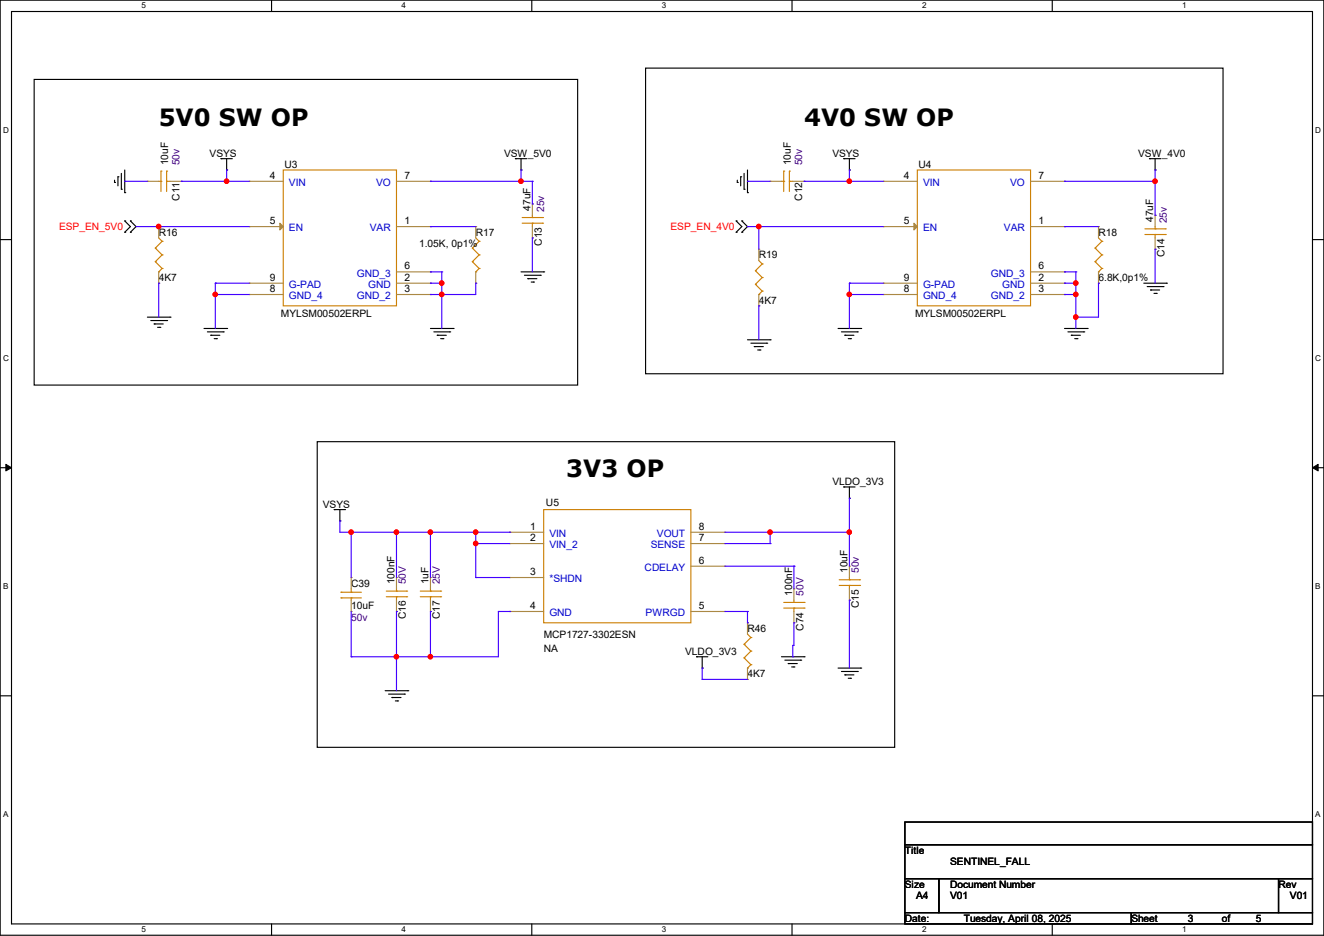
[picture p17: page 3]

# MICROCONTROLLER

# SIM800L

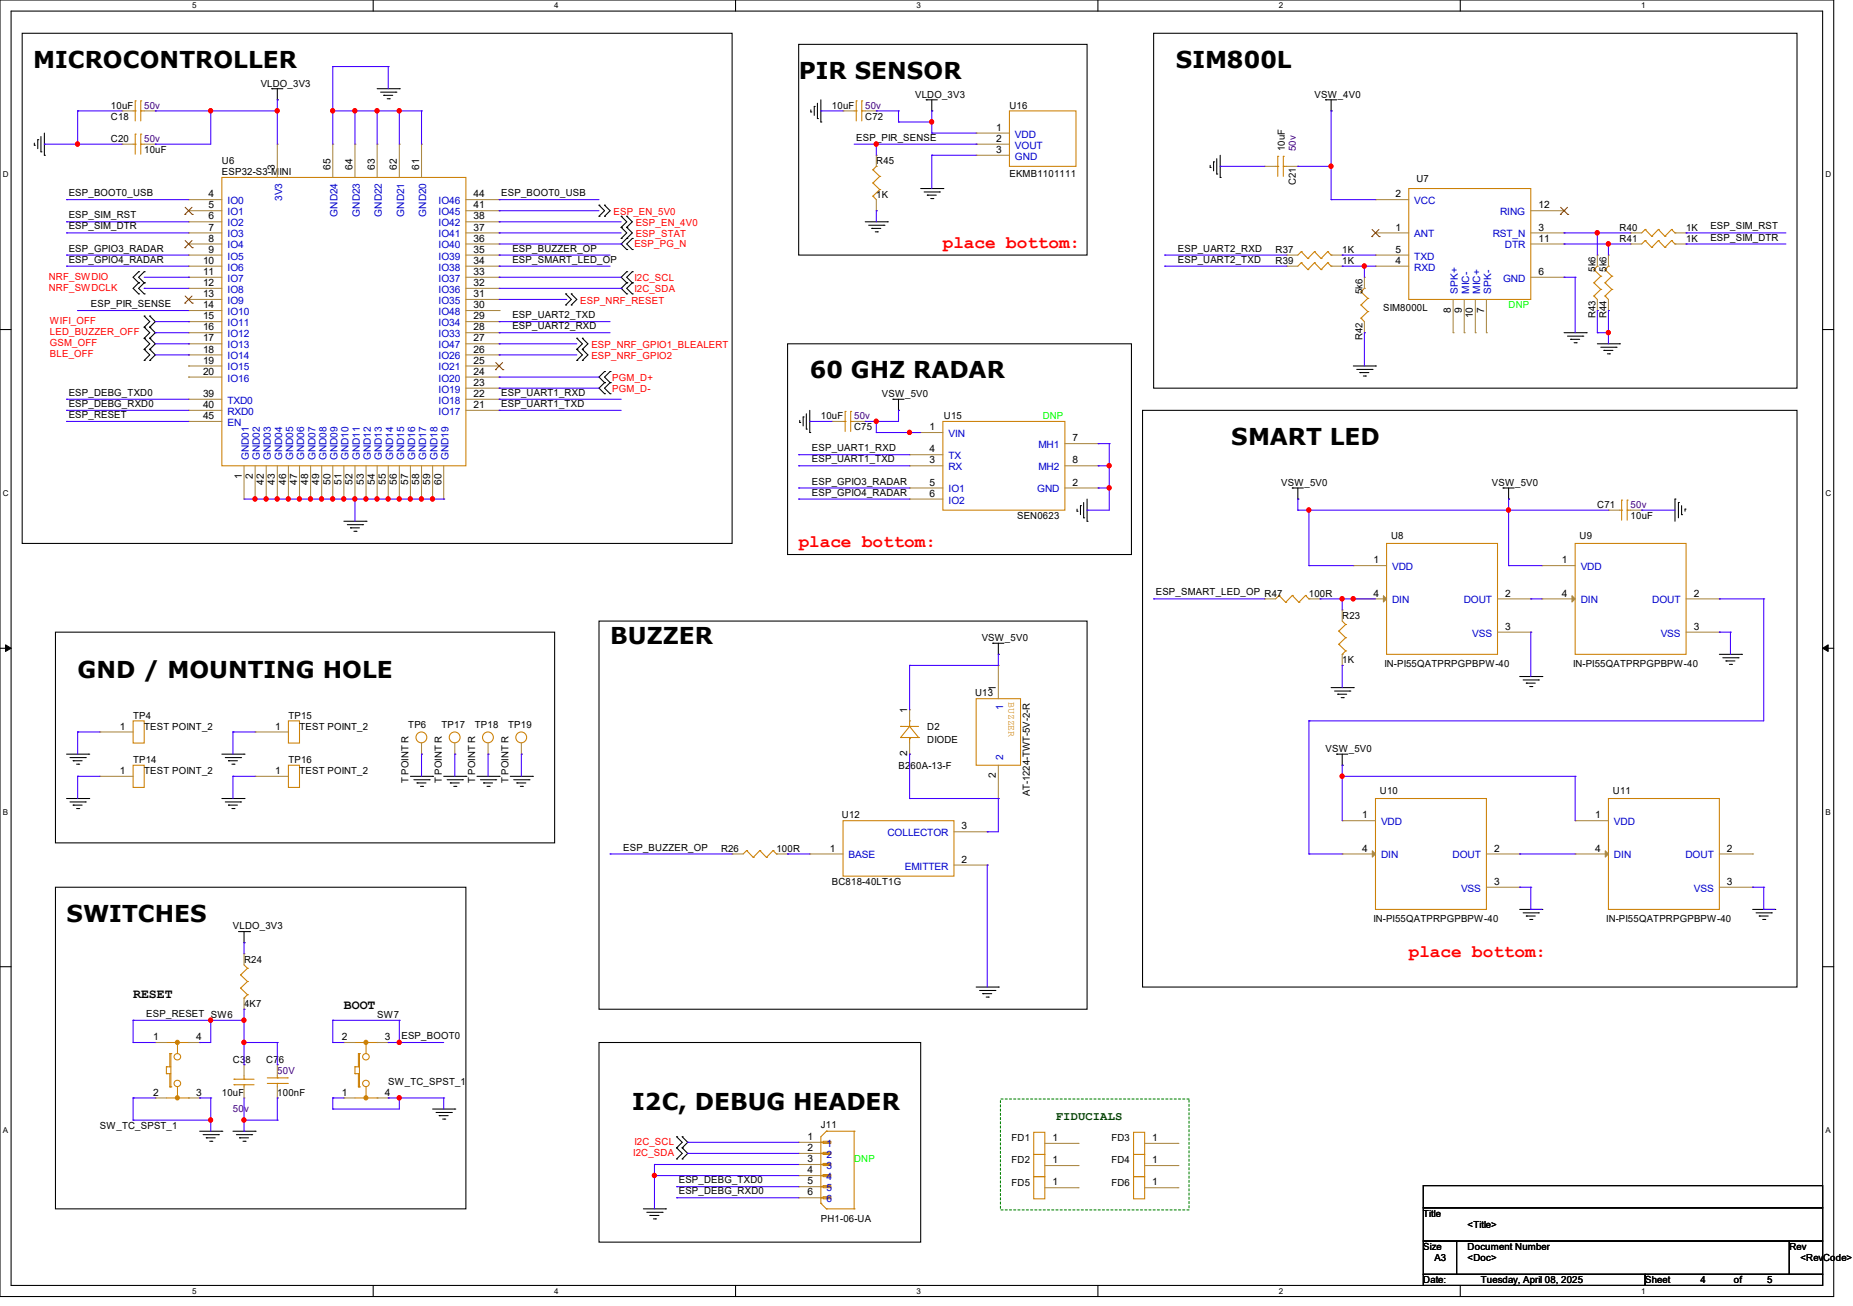
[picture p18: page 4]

8 MIC- 9 MIC+ 10 DTR 11 RING 12

# NRF54L15 MODULE

# DIP SWITCH - DISABLE FUNCTIONALITY

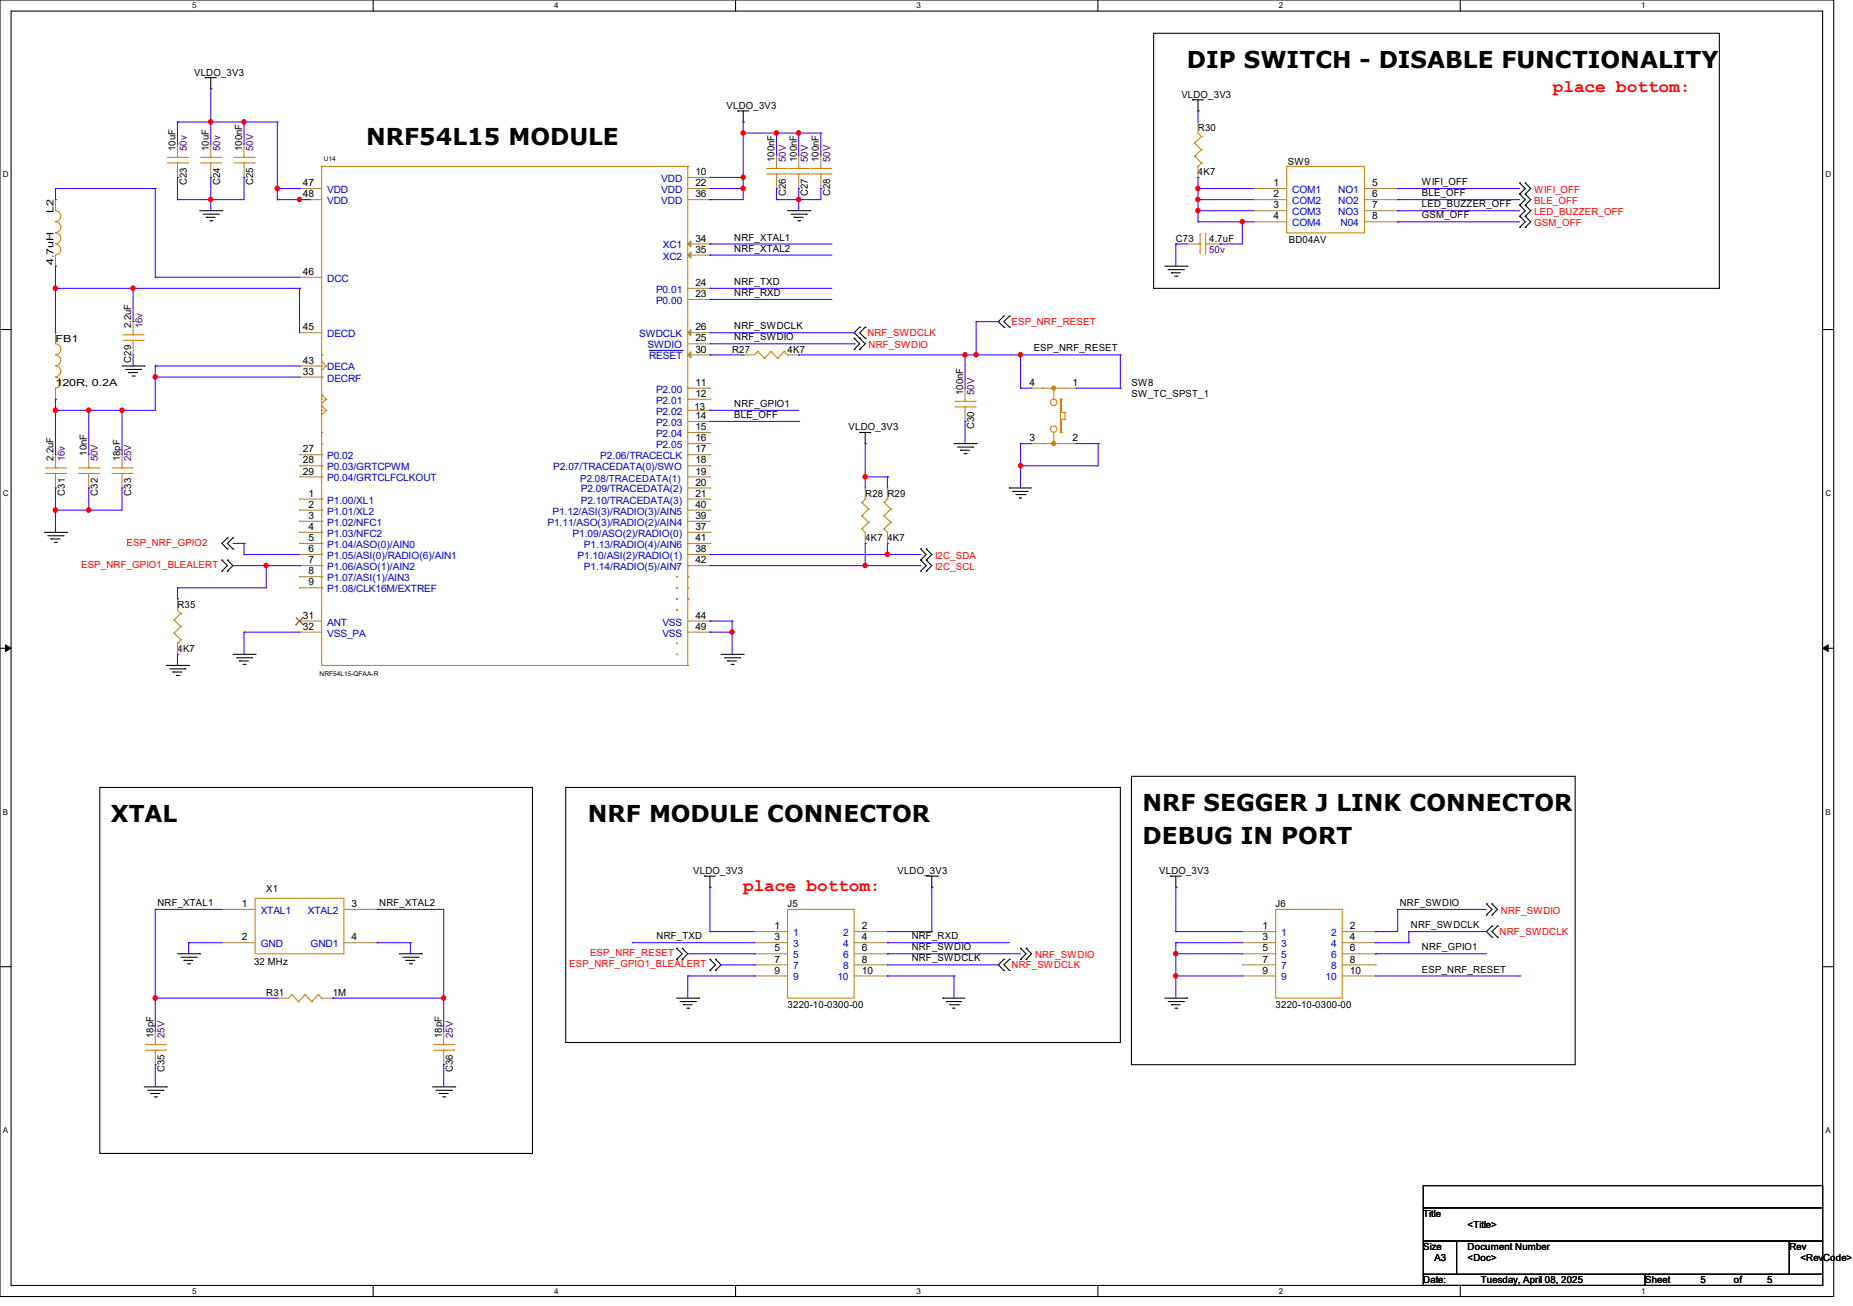
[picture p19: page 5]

NRF SEGGER J LINK CONNECTOR
DEBUG IN PORT

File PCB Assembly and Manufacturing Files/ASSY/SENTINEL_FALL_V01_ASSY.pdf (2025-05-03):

# ART FILM - AST

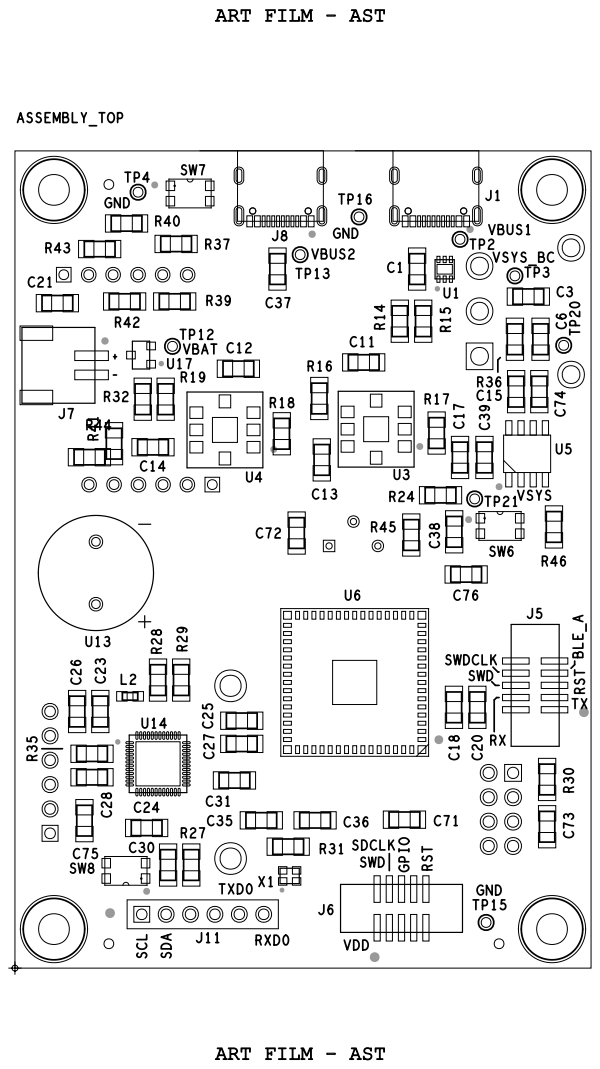
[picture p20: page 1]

# ART FILM - ASB

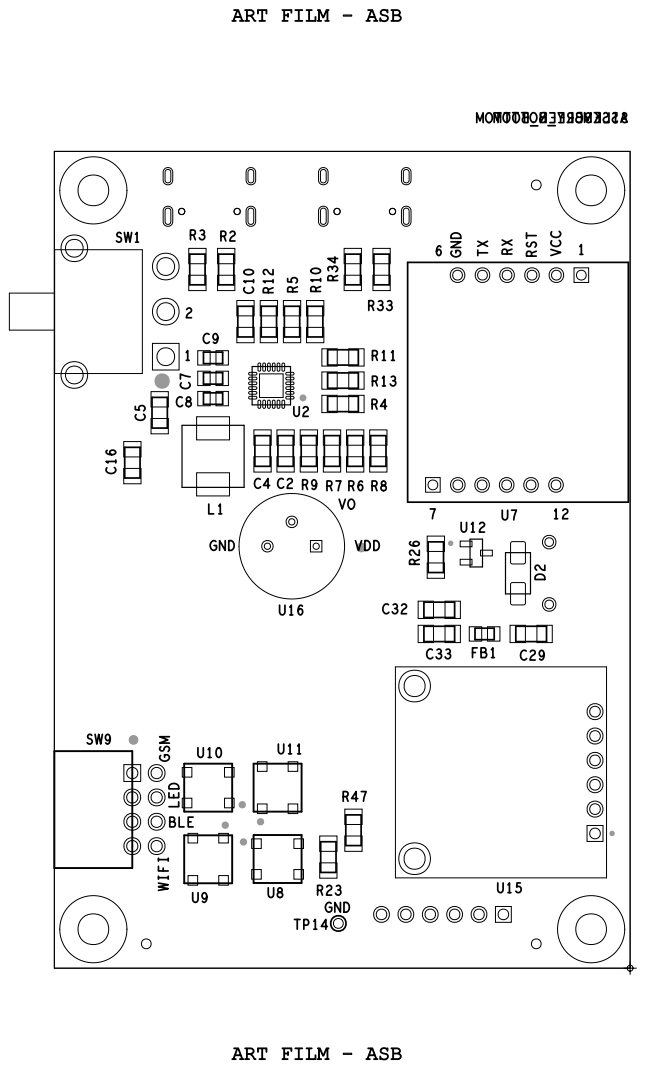
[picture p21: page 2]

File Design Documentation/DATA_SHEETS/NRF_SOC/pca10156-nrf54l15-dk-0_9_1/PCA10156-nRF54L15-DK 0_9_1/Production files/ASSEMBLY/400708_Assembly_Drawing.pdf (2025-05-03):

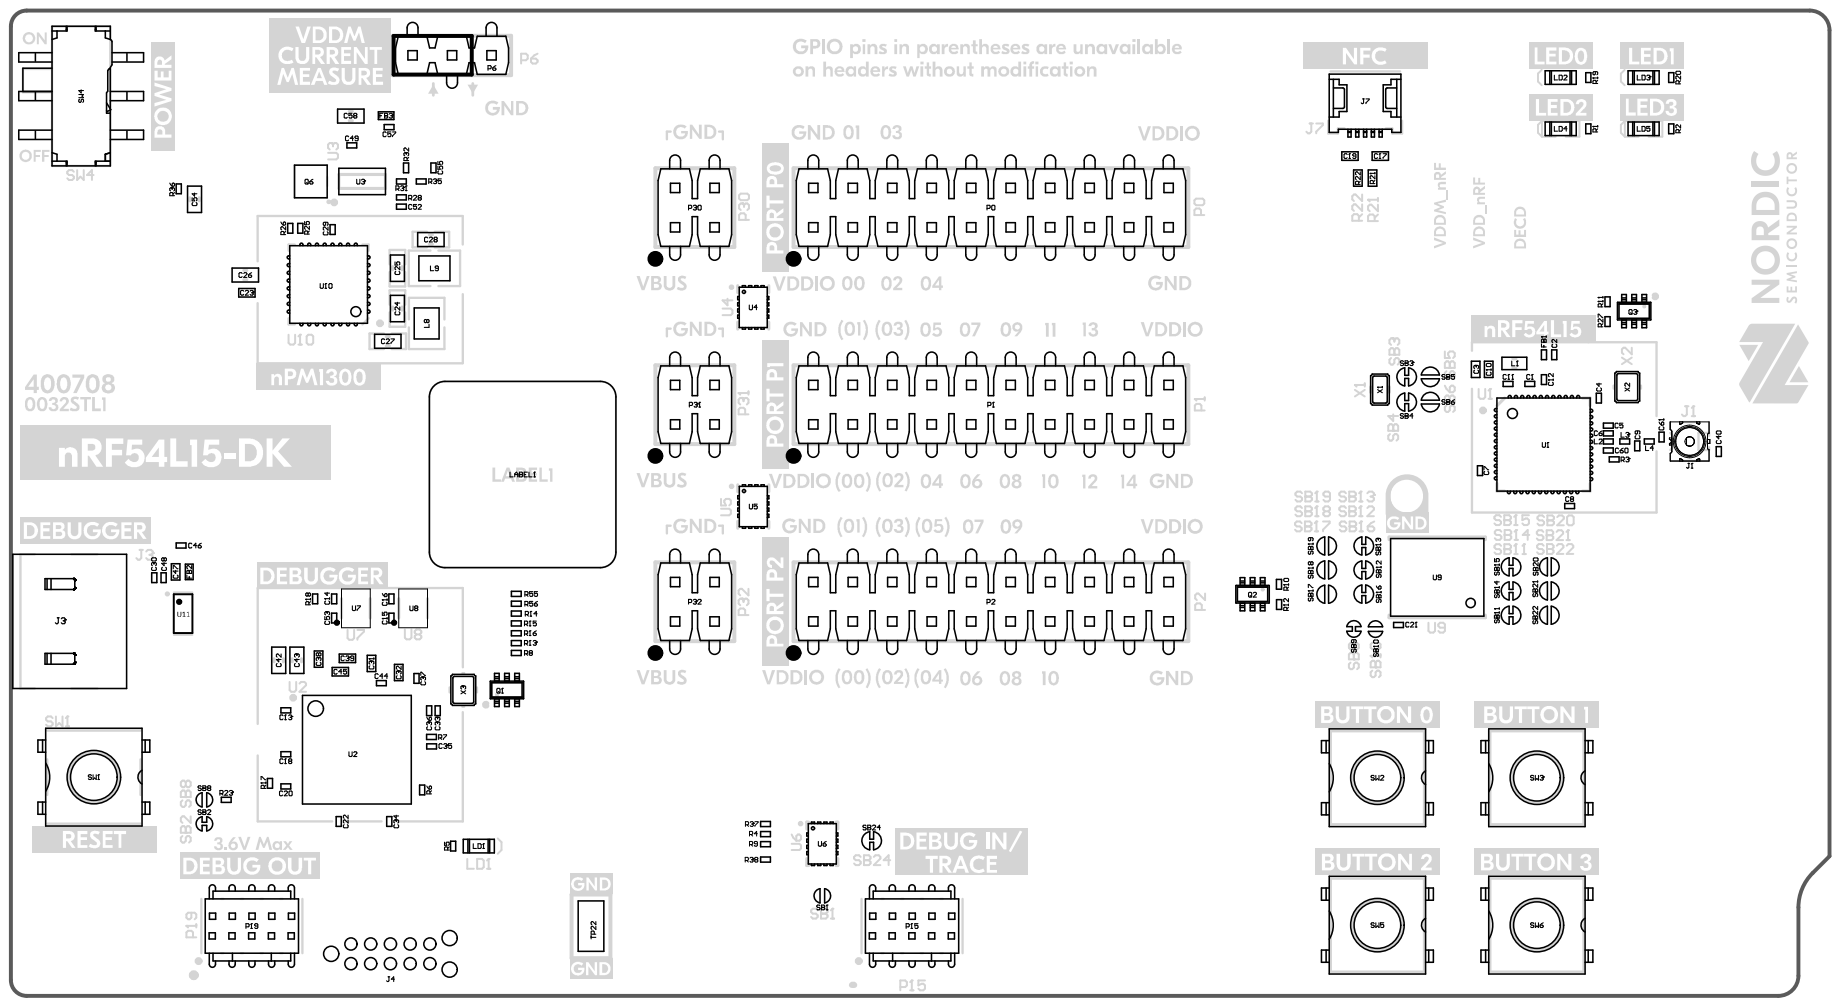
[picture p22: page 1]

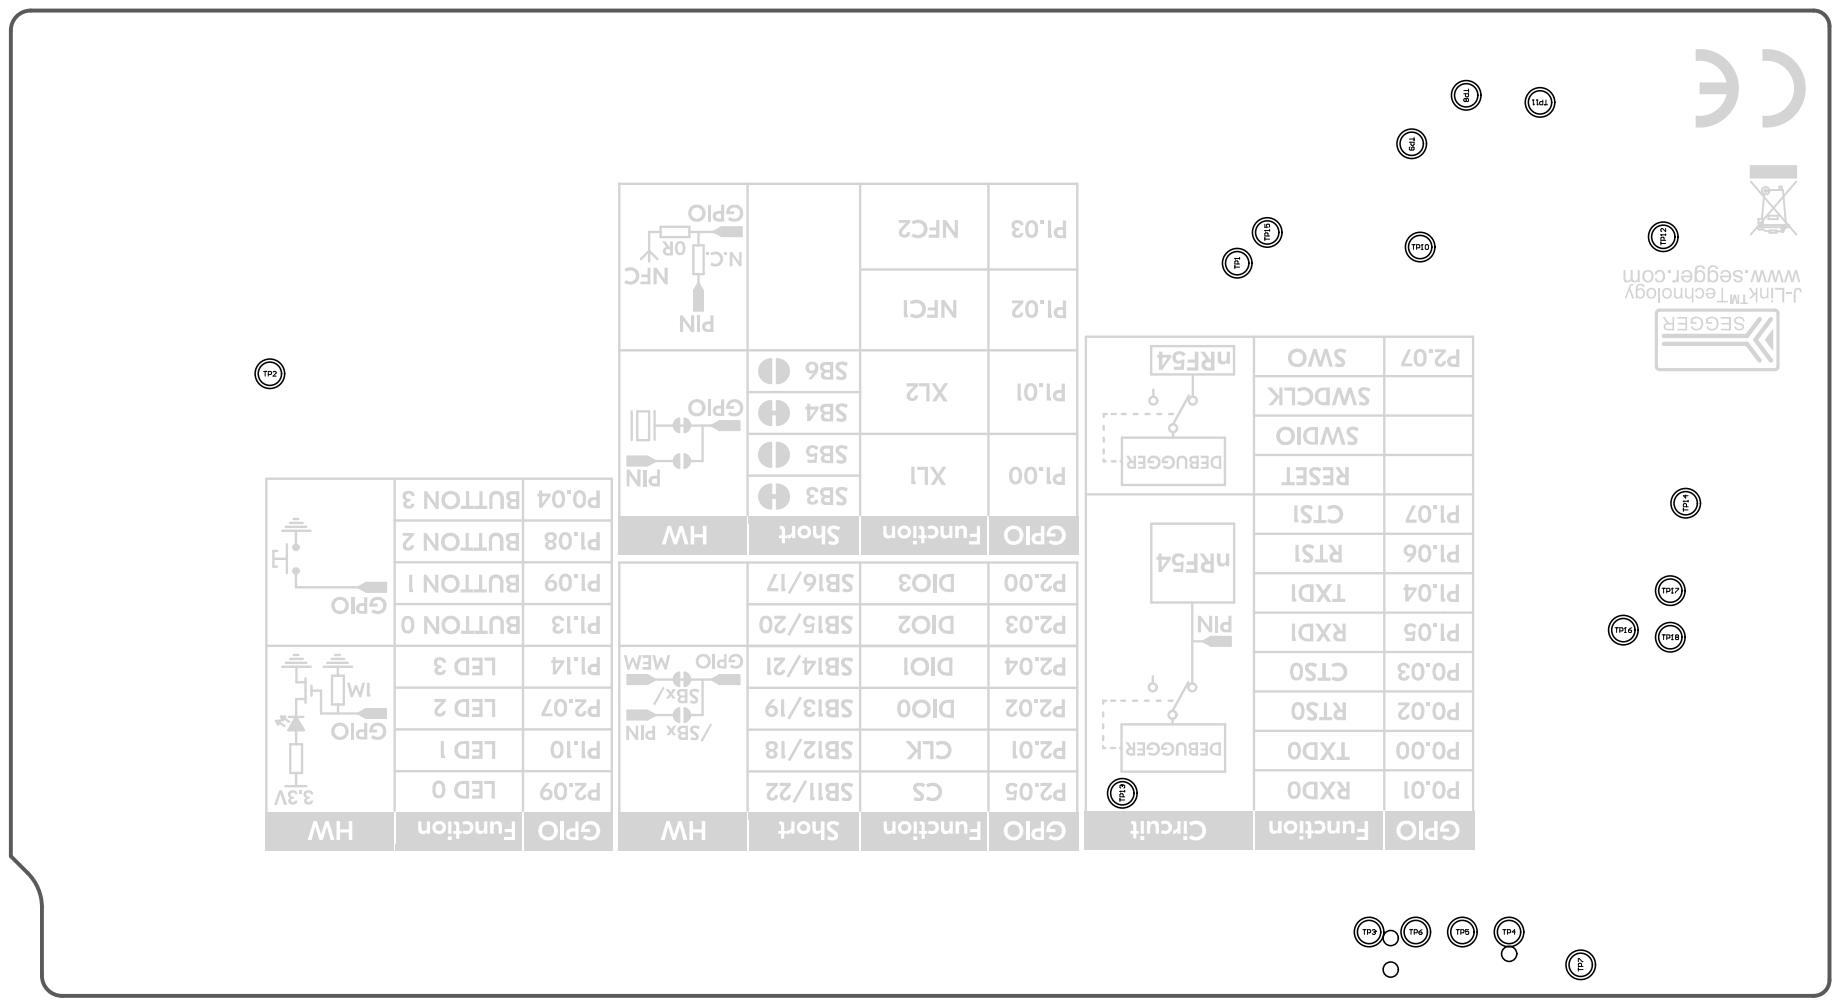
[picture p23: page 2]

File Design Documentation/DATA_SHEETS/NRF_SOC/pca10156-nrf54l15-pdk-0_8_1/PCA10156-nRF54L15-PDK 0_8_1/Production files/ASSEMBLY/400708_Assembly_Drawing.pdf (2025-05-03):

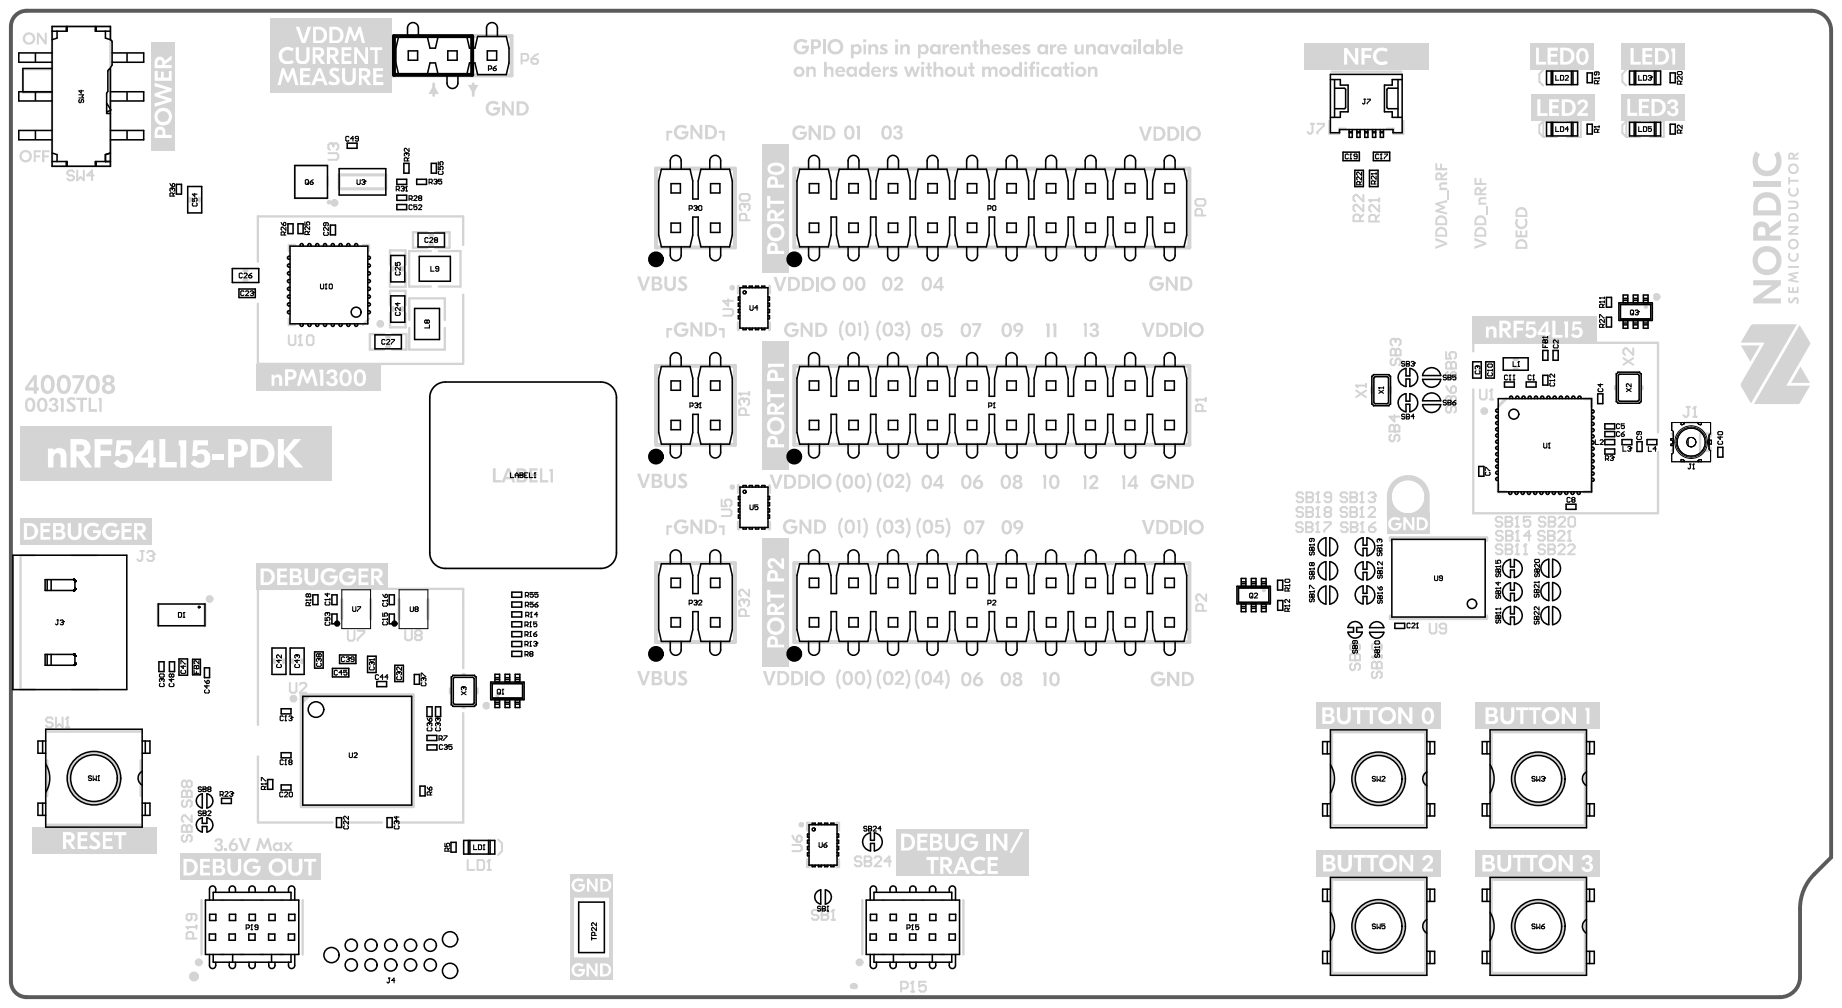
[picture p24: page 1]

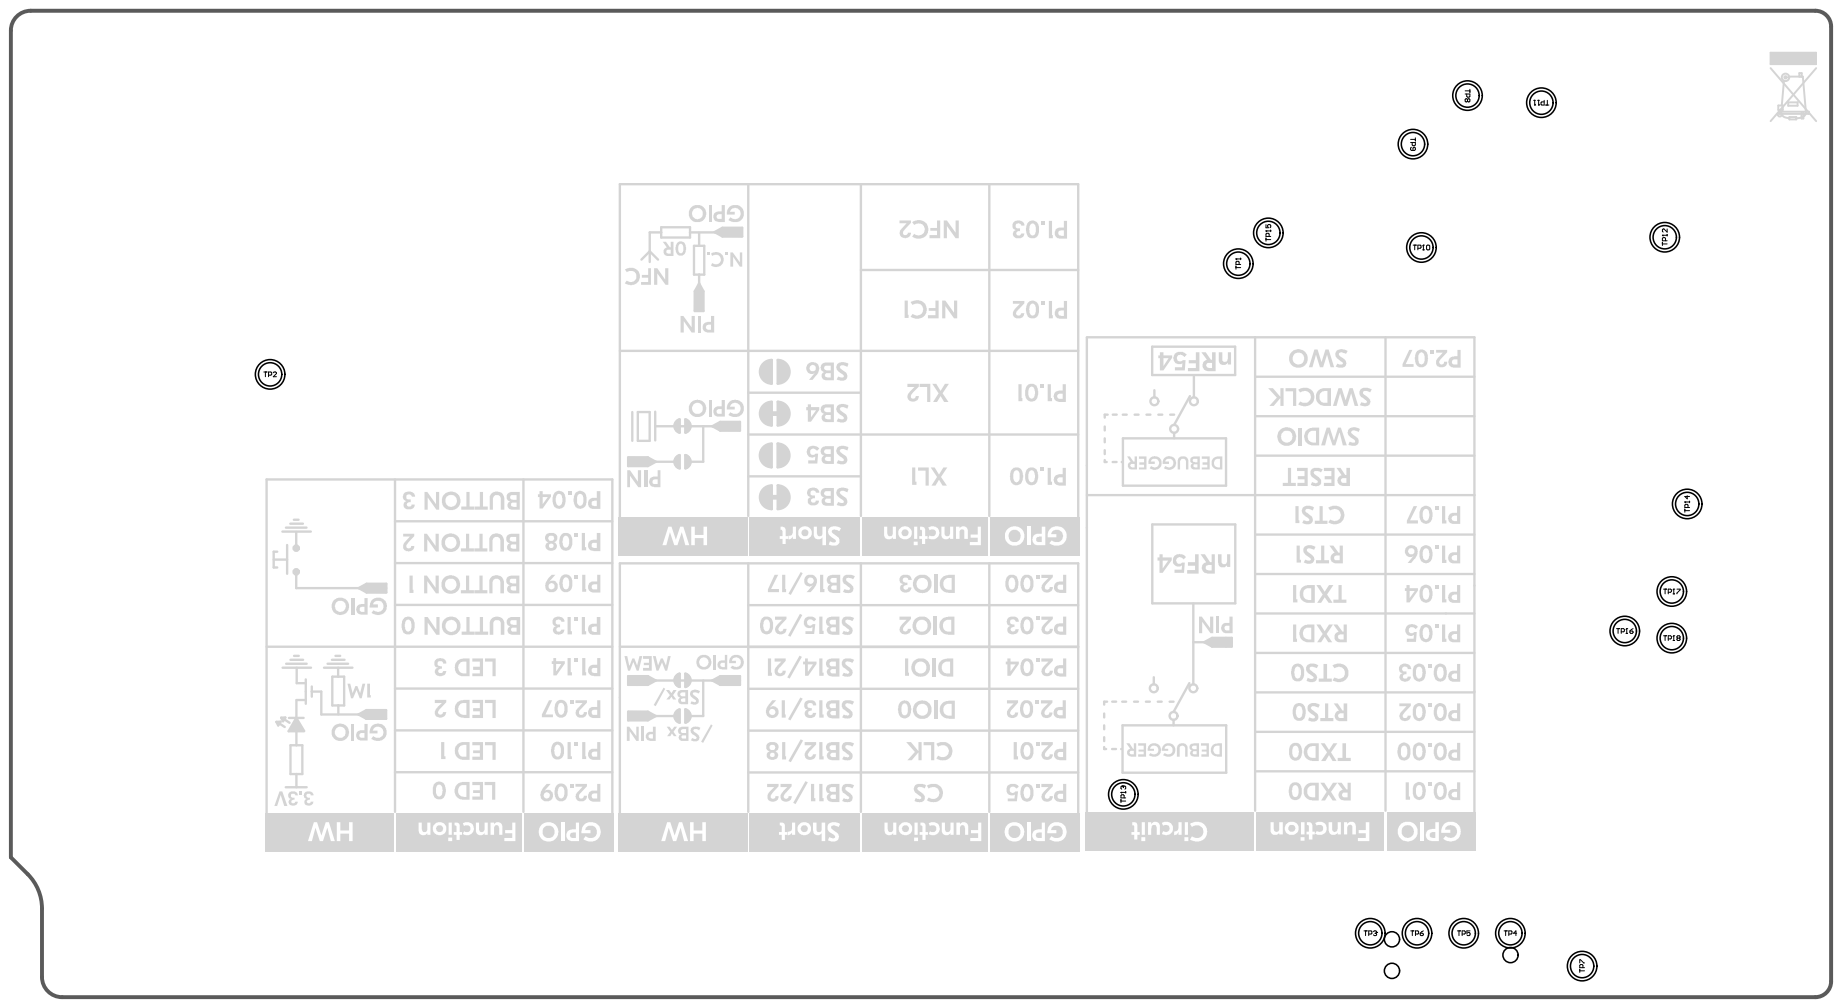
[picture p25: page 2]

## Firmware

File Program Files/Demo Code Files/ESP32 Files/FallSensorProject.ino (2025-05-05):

#include <WiFi.h>
#include <WebServer.h>
#include <ESP_Mail_Client.h>
#include "DFRobot_HumanDetection.h"

#define PIR_PIN 12 // GPIO pin connected to PIR sensor output


//// Replace with your WiFi credentials
const char *ssid = "wifi_name";// replace it with wifi name
const char *password = "PVPD515$"; // replace it with wifi password
// To send Emails using Gmail on port 465 (SSL), you need to create an app password: https://support.google.com/accounts/answer/185833
#define emailSenderAccount "fallsensoralert@gmail.com"
#define emailSenderPassword "asdfasdfasdfasdf" // replace it with gmail key
#define smtpServer "smtp.gmail.com"
#define smtpServerPort 465
#define emailSubject "Presence ALERT "

// Default Recipient Email Address
String inputMessage = "fallsensoralert@gmail.com";
String enableEmailChecked = "checked";
String inputMessage2 = "true";

// Flag variable to keep track if email notification was sent or not
bool emailSent = false;



// Access Point credentials
const char *ap_ssid = "ESP32-AP";
const char *ap_password = "12345678";
//
WebServer server(80);
// Radar object on Serial1
DFRobot_HumanDetection hu(&Serial1);
// SMTP session object
SMTPSession smtp;


// Web page handler
void handleRoot() {
  String html = "<html><body>";
  
  // Add existing information about human presence
  html += "<h2>Existing Information:</h2>";
  switch (hu.smHumanData(hu.eHumanPresence)) {
    case 0:
      html += "<p>No one is present</p>";
      break;
    case 1:
      html += "<p>Someone is present</p>";
      break;
    default:
      html += "<p>Read error</p>";
  }

  // Add motion information
  html += "<h2>Motion Information:</h2>";
  switch (hu.smHumanData(hu.eHumanMovement)) {
    case 0:
      html += "<p>None</p>";
      break;
    case 1:
      html += "<p>Still</p>";
      break;
    case 2:
      html += "<p>Active</p>";
      break;
    default:
      html += "<p>Read error</p>";
  }

//  // Add body movement parameters
//  html += "<h2>Body Movement Parameters:</h2>";
//  html += "<p>" + String(hu.smHumanData(hu.eHumanMovingRange)) + "</p>";

  // Add fall status
  html += "<h2>Fall Status:</h2>";
  switch (hu.getFallData(hu.eFallState)) {
    case 0:
      html += "<p>Not fallen</p>";
      break;
    case 1:
      html += "<p>Fallen</p>";
      break;
    default:
      html += "<p>Read error</p>";
  }

//  // Add stationary dwell status
//  html += "<h2>Stationary Dwell Status:</h2>";
//  switch (hu.getFallData(hu.estaticResidencyState)) {
//    case 0:
//      html += "<p>No stationary dwell</p>";
//      break;
//    case 1:
//      html += "<p>Stationary dwell present</p>";
//      break;
//    default:
//      html += "<p>Read error</p>";
//  }

  // Add PIR sensor status
  html += "<h2>PIR Sensor Status:</h2>";
  int pirValue = digitalRead(PIR_PIN);
  html += "<p>" + String(pirValue == HIGH ? "Motion Detected" : "No Motion") + "</p>";


  
  // Close the HTML tags
  html += "</body></html>";

  // Send the HTML response to the client
  server.send(200, "text/html", html);
}




void updateSerial()
{
  delay(500);
  while (Serial.available())
  {
    Serial2.write(Serial.read()); // Forward what Serial received to Software Serial Port
  }
  while (Serial2.available())
  {
    Serial.write(Serial2.read()); // Forward what Software Serial received to Serial Port
  }
}
bool waitForNetwork()
{
  String response = "";
  char c;
  while (true)
  {
    Serial2.println("AT+CREG?");
    delay(1000);

    response = "";
    while (Serial2.available())
    {
      c = Serial2.read();
      response += c;
    }
    Serial.print(response); // Print the module response to Serial monitor

    if (response.indexOf("+CREG: 0,1") != -1 || response.indexOf("+CREG: 0,5") != -1)
    {
      Serial.println("Network registered!");
      return true;
    }
    else
    {
      Serial.println("Waiting for network...");
      delay(2000);
    }
  }
}

void test_sim800_module()
{
  Serial2.println("AT");
  updateSerial();

  Serial2.println("AT+CMEE=2");
  updateSerial();

  Serial2.println("AT+CSQ");
  updateSerial();

  Serial2.println("AT+CCID");
  updateSerial();

  waitForNetwork(); // Wait until registered

  Serial2.println("ATI");
  updateSerial();

  Serial2.println("AT+CBC");
  updateSerial();
}

void send_SMS()
{
  Serial2.println("AT+CMGF=1"); // Set SMS to Text Mode
  updateSerial();

  Serial2.println("AT+CMGS=\"+13034722116\""); // Replace with your phone number
  delay(3000);                                 // Wait for '>' prompt
  updateSerial();

  Serial2.print("Circuit Digest"); // SMS body
  delay(500);
  Serial2.write(26); // ASCII code of CTRL+Z
  delay(1000);       // Wait for message to be sent
  Serial.println("Message Sent");
  updateSerial();
}

void setup()
{
  Serial.begin(115200);
  WiFi.mode(WIFI_STA);
    WiFi.begin(ssid, password);
    while (WiFi.waitForConnectResult() != WL_CONNECTED)
    {
      Serial.println("WiFi Failed!");
    }
  Serial2.begin(9600, SERIAL_8N1, 9, 10);    // RX=16, TX=17 (or any other valid pins)
  Serial1.begin(115200, SERIAL_8N1, 13, 15); // RX, TX

  Serial.println("Start initialization");
  while (hu.begin() != 0)
  {
    Serial.println("init error!!!");
    delay(1000);
  }
  Serial.println("Initialization successful");

  Serial.println("\nConnected to WiFi");
  Serial.print("STA IP: ");
  Serial.println(WiFi.localIP());

  // Start Access Point
  WiFi.softAP(ap_ssid, ap_password);
  Serial.print("AP IP: ");
  Serial.println(WiFi.softAPIP());

  // Web server endpoints
  server.on("/", handleRoot);

  Serial.println("Web server started");
  pinMode(PIR_PIN, INPUT);
  pinMode(22, OUTPUT);
  digitalWrite(22, LOW); 

  //  delay(1000 * 20);
  Serial.println("Statrtchecking");



  Serial.println("Start switching work mode");
  while (hu.configWorkMode(hu.eFallingMode) != 0)
  {
    Serial.println("error!!!");
    delay(1000);
  }
  Serial.println("Work mode switch successful");

  hu.configLEDLight(hu.eFALLLed, 1);        // Set HP LED switch, it will not light up even if the sensor detects a person present when set to 0.
  hu.configLEDLight(hu.eHPLed, 1);          // Set FALL LED switch, it will not light up even if the sensor detects a person falling when set to 0.
  hu.dmInstallHeight(10);                  // Set installation height, it needs to be set according to the actual height of the surface from the sensor, unit: CM.
  hu.dmFallTime(2);                         // Set fall time, the sensor needs to delay the current set time after detecting a person falling before outputting the detected fall, this can avoid false triggering, unit: seconds.
  hu.dmUnmannedTime(1);                     // Set unattended time, when a person leaves the sensor detection range, the sensor delays a period of time before outputting a no person status, unit: seconds.
  hu.dmFallConfig(hu.eResidenceTime, 20);   // Set dwell time, when a person remains still within the sensor detection range for more than the set time, the sensor outputs a stationary dwell status. Unit: seconds.
  hu.dmFallConfig(hu.eFallSensitivityC, 3); // Set fall sensitivity, range 0~3, the larger the value, the more sensitive.
  hu.sensorRet();                           // Module reset, must perform sensorRet after setting data, otherwise the sensor may not be usable.
  Serial.printf("Radar installation height: %d cm\n", hu.dmGetInstallHeight());
  Serial.printf("Fall duration: %d seconds\n", hu.getFallTime());
  Serial.printf("Unattended duration: %d seconds\n", hu.getUnmannedTime());
  Serial.printf("Dwell duration: %d seconds\n", hu.getStaticResidencyTime());
  Serial.printf("Fall sensitivity: %d \n", hu.getFallData(hu.eFallSensitivity));
  Serial.println();
  Serial.println();
}

void loop()
{
  int statusofpir = digitalRead(PIR_PIN);
  int humansensor = hu.smHumanData(hu.eHumanPresence);
  Serial.printf("%d,%d",statusofpir,humansensor);
  if ((statusofpir == 1 ) and (humansensor==1))
  {
    digitalWrite(22, HIGH);
    sendEmailNotification("Pressence Detected");
    Serial.println("BLE Alert send");
    
    digitalWrite(22, LOW);
  }
  server.handleClient();
}
bool sendEmailNotification(String emailMessage)
{
    String html = "<html><head><style>"
                  "body { font-family: Arial, sans-serif; margin: 20px; padding: 0; background-color: #f4f4f4; }"
                  "h2 { color: #4CAF50; font-size: 20px; }"
                  "p { font-size: 16px; color: #333; line-height: 1.6; }"
                  ".container { background-color: #ffffff; padding: 20px; border-radius: 8px; box-shadow: 0 2px 10px rgba(0, 0, 0, 0.1); max-width: 600px; margin: auto; }"
                  ".section { margin-bottom: 20px; }"
                  ".section p { background-color: #f9f9f9; padding: 10px; border-radius: 5px; }"
                  "</style></head><body>";

    html += "<div class='container'>";  // Start container to center the content and add padding

    // Add existing information about human presence
    html += "<div class='section'><h2>Existing Information:</h2>";
    switch (hu.smHumanData(hu.eHumanPresence)) {
        case 0:
            html += "<p>No one is present</p>";
            break;
        case 1:
            html += "<p>Someone is present</p>";
            break;
        default:
            html += "<p>Read error</p>";
    }
    html += "</div>";

    // Add motion information
    html += "<div class='section'><h2>Motion Information:</h2>";
    switch (hu.smHumanData(hu.eHumanMovement)) {
        case 0:
            html += "<p>None</p>";
            break;
        case 1:
            html += "<p>Still</p>";
            break;
        case 2:
            html += "<p>Active</p>";
            break;
        default:
            html += "<p>Read error</p>";
    }
    html += "</div>";

    
    html += "<div class='section'><h2>BLE Alert:</h2>";
    html += "<p>Sent</p>";
    html += "</div>";


    // Add fall status
    html += "<div class='section'><h2>Fall Status:</h2>";
    switch (hu.getFallData(hu.eFallState)) {
        case 0:
            html += "<p>Not fallen</p>";
            break;
        case 1:
            html += "<p>Fallen</p>";
            break;
        default:
            html += "<p>Read error</p>";
    }
    html += "</div>";

    // Add PIR sensor status
    html += "<div class='section'><h2>PIR Sensor Status:</h2>";
    int pirValue = digitalRead(PIR_PIN);
    html += "<p>" + String(pirValue == HIGH ? "Motion Detected" : "No Motion") + "</p>";
    html += "</div>";

    html += "</div></body></html>";  // Close container and body

    // Configure the session
    ESP_Mail_Session session;
    session.server.host_name = smtpServer;
    session.server.port = smtpServerPort;
    session.login.email = emailSenderAccount;
    session.login.password = emailSenderPassword;
    session.login.user_domain = "";

    // Configure the message
    SMTP_Message message;
    message.sender.name = "ESP32";
    message.sender.email = emailSenderAccount;
    message.subject = emailSubject;
    message.addRecipient("Recipient", inputMessage);
    message.html.content = html.c_str();  // Use HTML content
    message.html.charSet = "utf-8";
    message.html.transfer_encoding = Content_Transfer_Encoding::enc_7bit;
    message.priority = esp_mail_smtp_priority::esp_mail_smtp_priority_high;

    // Set the callback function
    smtp.callback(smtpCallback);

    // Connect to the server and send the email
    if (!smtp.connect(&session)) {
        Serial.println("Failed to connect to SMTP server: " + smtp.errorReason());
        return false;
    }

    if (!MailClient.sendMail(&smtp, &message)) {
        Serial.println("Error sending Email: " + smtp.errorReason());
        smtp.closeSession();
        return false;
    }

    smtp.closeSession();
    return true;
}
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

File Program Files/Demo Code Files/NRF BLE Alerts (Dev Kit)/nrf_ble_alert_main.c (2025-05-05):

/*
 * Copyright (c) 2018 Nordic Semiconductor ASA
 *
 * SPDX-License-Identifier: LicenseRef-Nordic-5-Clause
 */

/** @file
 *  @brief  Nordic UART Bridge Service (NUS) sample with Custom Message alert based on GPIO Pin
 *  @author Abhirath Koushik (abhirathkoushik-cub)
 */

/**
 * Modifications:
 * - Congfigured Button-0 and its linked GPIO Pin to connect with the external circuit.
 * - Created bt_hello_thread() function to send the Custom message using the existing APIs in this script.
 *
 * @author Abhirath Koushik (abhirathkoushik-cub)
 */

#include <uart_async_adapter.h>

#include <zephyr/types.h>
#include <zephyr/kernel.h>
#include <zephyr/drivers/uart.h>
#include <zephyr/usb/usb_device.h>
#include <zephyr/drivers/gpio.h>

#include <zephyr/device.h>
#include <zephyr/devicetree.h>
#include <soc.h>

#include <zephyr/bluetooth/bluetooth.h>
#include <zephyr/bluetooth/uuid.h>
#include <zephyr/bluetooth/gatt.h>
#include <zephyr/bluetooth/hci.h>

#include <bluetooth/services/nus.h>

#include <dk_buttons_and_leds.h>

#include <zephyr/settings/settings.h>

#include <stdio.h>
#include <string.h>

#include <zephyr/sys/util.h>
#include <zephyr/sys/printk.h>
#include <inttypes.h>

#include <zephyr/logging/log.h>

#define LOG_MODULE_NAME peripheral_uart
LOG_MODULE_REGISTER(LOG_MODULE_NAME);

#define STACKSIZE CONFIG_BT_NUS_THREAD_STACK_SIZE
#define PRIORITY 7

#define DEVICE_NAME CONFIG_BT_DEVICE_NAME
#define DEVICE_NAME_LEN	(sizeof(DEVICE_NAME) - 1)

#define RUN_STATUS_LED DK_LED1
#define RUN_LED_BLINK_INTERVAL 1000

#define CON_STATUS_LED DK_LED2

#define KEY_PASSKEY_ACCEPT DK_BTN1_MSK
#define KEY_PASSKEY_REJECT DK_BTN2_MSK

#define UART_BUF_SIZE CONFIG_BT_NUS_UART_BUFFER_SIZE
#define UART_WAIT_FOR_BUF_DELAY K_MSEC(50)
#define UART_WAIT_FOR_RX CONFIG_BT_NUS_UART_RX_WAIT_TIME

#define SW0_NODE	DT_ALIAS(sw0)
static const struct gpio_dt_spec button = GPIO_DT_SPEC_GET_OR(SW0_NODE, gpios, {0});
static struct gpio_callback button_cb_data;
static struct gpio_dt_spec led = GPIO_DT_SPEC_GET_OR(DT_ALIAS(led0), gpios, {0});

static K_SEM_DEFINE(ble_init_ok, 0, 1);

static struct bt_conn *current_conn;
static struct bt_conn *auth_conn;

static const struct device *uart = DEVICE_DT_GET(DT_CHOSEN(nordic_nus_uart));
static struct k_work_delayable uart_work;

struct uart_data_t {
	void *fifo_reserved;
	uint8_t data[UART_BUF_SIZE];
	uint16_t len;
};

static K_FIFO_DEFINE(fifo_uart_tx_data);
static K_FIFO_DEFINE(fifo_uart_rx_data);

static const struct bt_data ad[] = {
	BT_DATA_BYTES(BT_DATA_FLAGS, (BT_LE_AD_GENERAL | BT_LE_AD_NO_BREDR)),
	BT_DATA(BT_DATA_NAME_COMPLETE, DEVICE_NAME, DEVICE_NAME_LEN),
};

static const struct bt_data sd[] = {
	BT_DATA_BYTES(BT_DATA_UUID128_ALL, BT_UUID_NUS_VAL),
};

#ifdef CONFIG_UART_ASYNC_ADAPTER
UART_ASYNC_ADAPTER_INST_DEFINE(async_adapter);
#else
#define async_adapter NULL
#endif

void button_pressed(const struct device *dev, struct gpio_callback *cb,
	uint32_t pins)
{
printk("Button pressed at %" PRIu32 "\n", k_cycle_get_32());
}
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

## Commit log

2025-05-03 ADDED FILESNTIAL COMIT ADDED NIKH FILES
    [400708.DRL, 400708.GBL, 400708.GBO, 400708.GBP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]
2025-05-05 adding the readme to esp32 folder
2025-05-05 esp32 code
